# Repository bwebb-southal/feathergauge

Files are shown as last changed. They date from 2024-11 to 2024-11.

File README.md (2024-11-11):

# DIY Feather v4 Standard Operating Procedures 

Bret Webb (bwebb@southalabama.edu)

GitHub: https://github.com/bwebb-southal/feathergauge 

DesignSafe: coming soon

## Arduino IDE Preparation
If you have zero experience using the Arduino IDE, please refer to these tutorials [here](https://www.arduino.cc/en/Tutorial/HomePage)

1. Enable support for Adafruit boards in the Preferences menu by following [these directions](https://learn.adafruit.com/adafruit-feather-32u4-adalogger/setup)

1. Add support for the Adafruit AVR boards using Board Manager under Tools/Boards using [these instructions](https://learn.adafruit.com/adafruit-feather-32u4-adalogger/setup)

1. Select the Adafruit Feather 32u4 under Tools / Board

1. If this is your first time setting up your Arduino environment, you’ll need to add the necessary libraries. Libraries are managed using Tools / Manage Libraries in the Arduino IDE. The Nov2024 versions of the logger code sketches are compatible with the following libraries, and all of these need to be installed on your computer:

    a. Blue Robotics MS5837 v1.1.1

    b. SD v1.3.0

    c. RTClib v2.1.4

    d. TimerOne v1.1.1

1. Add the logger code sketch to your default Arduino Sketchbook location folder… note that the code sketch must reside in a folder of the same name as the sketch… this is required! The Arduino Sketchbook location folder was established during the setup process when you installed the Arduino IDE software. However, it can be redefined at any time. This is defined in your Arduino IDE Preferences menu (File / Preferences).

1. Ensure device is recognized in Tools/Port and select it. If you do not see your device, refer to Troubleshooting below. 

>[!NOTE]
> Ensure that your files and software are installed on your computer and not in a cloud-based segment of your PC or Mac. We have observed inconsistent behavior when using cloud-based folders. Note that many new PCs, specifically laptops, will default to cloud-based or cloud-connected folders on your system. If your Arduino Sketchbook location folder is not defined in a path structure on your physical hard drive, things may not work very well.

## Deployment Preparation 
Here are step-by-step instructions for preparing a DIY Feather v4 wave gauge for deployment. These steps assume that you already have your Arduino and environment prepared. If this is your first time using the gauge, please refer to the section at the end of this document regarding Arduino IDE Preparation. 

1. charge the battery (plug the battery into the USB charging adapter, or plug the battery into the board and then plug the board into a computer or USB outlet)

1. check the RTC
   
    a. Connect the board to the computer
  
    b. Open the Arduino software
  
    c. Open the sketch File/Examples/RTClib/ds3231
  
    d. Compile and upload the sketch to your board
  
    e. Open the serial monitor in the Arduino IDE (Tools / Serial Monitor) and confirm the date and time
  
    f. If the date/time is incorrect, uncomment line #25 then repeat steps 2d and 2e
  
    g. If the clock is still not correct, proceed to 3 below

1. reset the RTC

    a. remove coin cell battery for at least 60 seconds then replace it
  
    b. repeat steps 2c-2e

1. upload logger sketch

    a. There are four possible logger sketches as of Nov 2024: 1) rapid start with user-defined sampling rate; 2) delayed start with user-defined sampling rate; 3) rapid start with burst sampling; 4) delayed start with burst sampling
  
    b. Be sure to define your desired parameter values in the /* User Inputs */ section of each code sketch

1. allow DIY gauge to sample for about 60 s

1. disconnect usb 

1. remove microsd

1. insert microsd card into your computer

1. check data file and confirm that date/time and pressure (and/or temperature) are correct

1. remove data file(s)

1. reinsert microsd card into board

## Deployment 
When you are ready to deploy the gauge, follow these steps…

1. plug in the battery 

1. confirm LED flashing* (as of versions labeled _v1):

    a. rapid start, continuous sampling: solid green for about the first ~10 seconds then no other LEDs

    b. Rapid start, burst sampling: solid green during burst sampling; solid red during sleep interval 

    c. delayed start, continuous sampling: flashing red for ~20 seconds before start time; solid green for about the first ~10 seconds of continuous sampling

    d. delayed start, burst sampling: flashing red for ~20 seconds before start time; solid green during burst sampling; solid red while sleeping in between bursts

1. insert components into gauge housing along with a small desiccant pack

1. allow to sample** in atmospheric pressure for at least 1-2 minutes

1. place all prepared gauges in a bucket filled with your seawater (preferably from your deployment location but freshwater will do) and allow to sample** for at least 1-2 minutes. Ensure all sensors are oriented similarly (sensor at the bottom of the bucket).
   
1. deploy sensor making sure you keep depth attenuation in mind… see guidance below.

    a. Basically, you need to ensure your pressure sensor will detect the dynamic pressure fluctuations of your shortest wave periods, which attenuate quickly over the water column. 

    b. Figure 1 below shows the pressure decay coefficient as a function of wave period and water depth for four different deployment elevations (above the bed). You want to keep your decay coefficient as close to 1 as possible. You definitely want to stay out of the blue areas in these figures.

    c. Example: if you deploy a gauge on the bed in 3 m of water, you won’t detect any dynamic pressure (or hardly any) for wave periods less than or equal to 2 s. 

1. recommend deploying the gauge horizontally or vertically, and if vertically do so with sensor port pointing downward 

>[!NOTE]
> In step 2: if you would like to conserve more battery power, disabling the LED flashing is a fairly simple task. Any/all commands labeled “digitalWrite(----)” within the void loop() structure can be commented out with no impact to the code operation whatsoever. To comment (i.e., disable) out the LED blinking, simply place your cursor on the line of code (to the left of) containing the active digitalWrite(8, xxx) or digitalWrite(13, xxx) command, then select Edit / Comment/Uncomment from the Arduino IDE menu. If the line is active, it will become inactive, you’ll see  two “//” before the statement, and the text will turn gray. To reactivate that line of code, either remove the “//” or select Edit / Comment/Uncomment again and the line of code will become active once again.

>[!NOTE]
> In steps 4-5: this only makes sense if you are using the rapid start version of the logger code sketches. If you are using the rapid start code with burst sampling, make sure you are logging atmospheric and bucket test pressures during your burst interval (refer to LED flashing codes above for reference). If you are using the delayed start version of the code sketches, it may not be possible to sample atmospheric or bucket test pressures prior to deployment. If that is the case, I strongly recommend doing these things at the end of your deployment (before removing the battery). The atmospheric and bucket test pressure samples allow you to perform minor corrections to ensure consistent measurement values across your gauges. The inexpensive pressure sensors seem to have small offsets that, while not necessary, could be advantageous to correct by comparing their values under static conditions.

pressuredecayguide
Figure 1. Deployment Guidance for Pressure Attenuation with Depth

## Post-Deployment Recovery
Here are some suggested step-by-step procedures to consider after you retrieve your DIY wave gauge…

1. do not open gauge before cleaning thoroughly 

1. submerge gauge in a bucket of warm water mixed with distilled white vinegar (and dish soap if you like, but the dish soap is not necessary)

1. if gauges are considerably fouled, consider adding baking soda as this will combine with the vinegar to produce strong agitation and fizzing (definitely do not use dish soap here)

1. do not touch the gel membrane inside of the pressure sensor no matter what you do 

1. remove from cleaning bath and wipe dry

1. remove cap 

1. inspect for signs of moisture 

1. remove internal components 

1. disconnect battery 

1. remove microsd card

## Post-Processing 
The gauge data will be saved to CSV files on the microsd card. Post-processing the pressure data can be done in a variety of ways. We have posted some example post-processing scripts written in MATLAB. If you don’t have access to MATLAB you might find your own alternative method for processing the data. Just remember that the pressure values are absolute… so you need to subtract out atmospheric pressure. Ideally, you would have an atmospheric reference nearby so that you have a time-series of data, but in a pinch you can use an average/estimated value of atmospheric pressure. Each millibar of atmospheric pressure corresponds to (approximately) 1 cm of water height change. 

1. insert microsd card into your computer 

1. save the files to your computer

1. run the MATLAB post-processing scripts or process using your own codes

## Troubleshooting

1. My board isn’t recognized by Arduino IDE: make sure you are using a power+data cable… many micro USB cables are power only… if the device is not recognized as a com port under device manager (windows) then you’re probably using a power only cable.

1. My board isn’t recognized by Arduino IDE and I am sure that I am using an appropriate power+data cable: try resetting the bootloader on the feather logger board (see below).

1. I need to reset my bootloader: you’ll need access to the small black reset button located near the micro USB plug on top of the board. With the board plugged in, open the blink sketch found in File / Examples / Basics / Blink. Click the compile/upload “arrow” icon. Immediately double tap the reset button. This should resolve the issue. You may need to do this a few times. 

1. My date/time are incorrect: refer to 2 and 3 in the Deployment Preparation section above.

1. My logger isn’t working correctly: try uploading something simple like File / Examples / Basics / Blink. Does that work? If not, there’s likely an issue with your board. If yes, see below.

1. My logger still isn’t working: 

    a. Check your microsd card. Is it installed correctly? Are you using the recommended 8gb microsd card? If not, this may be the issue. The logger cannot handle large microsd cards.

    b. Check your wiring. 

    c. Perform a continuity check.

1. My logger is writing to the microsd card, but the values don’t make sense.

    a. Check your wiring… make sure you did not reverse the SCL and SDA wires.

    b. Try using the simple sketch provided by the MS5837 pressure sensor manufacturer by going to File / Examples / BlueRobotics MS5837 Library / MS5837_example. Before uploading, you’ll need to change one line in the code. Refer to the line with…

    ```
      sensor.setModel(MS5837::MS5837_30BA);
    ```
    and change the _30BA to _02BA as follows…
    ```
	    sensor.setModel(MS5837::MS5837_02BA);
    ```
    then open Serial Monitor and see if the values make sense.

1. open for addressing future issues…

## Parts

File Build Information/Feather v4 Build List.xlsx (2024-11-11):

USA Feather Logger v4 Parts List
ITEM | NAME | UNIT COST | UNITS | TOTAL ITEM COST | LINK
1 | Adafruit Feather 32u4 Adalogger | $21.95 | 1 | $21.95 | https://www.adafruit.com/product/2795
2 | Adafruit DS3231 Precision RTC - STEMMA QT | $13.95 | 1 | $13.95 | https://www.adafruit.com/product/5188
3 | STEMMA QT / Qwiic JST SH 4-Pin Cable - 50mm Long | $0.95 | 1 | $0.95 | https://www.adafruit.com/product/4399
4 | STEMMA QT / Qwiic JST SH 4-Pin Cable - 200mm Long | $1.25 | 1 | $1.25 | https://www.adafruit.com/product/4401
5 | Lithium Ion Battery Pack 3.7V 4400 mAh | $19.95 | 1 | $19.95 | https://www.adafruit.com/product/354
6 | Micro Lipo-USB Lilon/LiPoly charger v2 | $5.95 | 1 | $5.95 | https://www.adafruit.com/product/1304
7 | CR1220 12mm Diameter Coin Cell Battery | $0.95 | 1 | $0.95 | https://www.adafruit.com/product/380
8 | SD/MicroSD Memory Card 86B SDHC | $9.95 | 1 | $9.95 | https://www.adafruit.com/product/1294
9 | Bar02 Ultra High Resolution 10m Depth/Pressure Sensor | $75.00 | 1 | $75.00 | https://bluerobotics.com/store/sensors-cameras/sensors/bar02-sensor-r1-rp/
10 | 1.5" PVC Pipe | $2.17 | 0.67 | $1.45 | https://www.lowes.com/pd/Charlotte-Pipe-1-1-2-in-dia-x-5-ft-L-330-PSI-PVC-Pipe/3133039
11 | 1-1/2-in dia PVC Female Adapter Fitting | $2.29 | 1 | $2.29 | https://www.lowes.com/pd/Charlotte-Pipe-1-1-2-in-x-1-1-2-in-dia-PVC-Schedule-40-Female-Adapter-Fitting/3132709
12 | 1-1/2-in PVC DWV Male Plug | $1.69 | 1 | $1.69 | https://www.lowes.com/pd/Charlotte-Pipe-1-1-2-in-x-1-1-2-in-dia-PVC-Schedule-40-Male-Cleanout-Plug-Fitting/3354904
13 | Oatey 1-1/2-in Gripper PVC DWV Test Plug | $5.65 | 1 | $5.65 | https://www.lowes.com/pd/Oatey-Gripper-1-1-2-in-x-1-1-2-in-x-1-1-2-in-x-1-1-2-in-dia-PVC-Schedule-40-Test-Plug-Fitting/3824165
14 | PVC Glue & Primer | $11.68 | 0.01 | $0.12 | https://www.lowes.com/pd/Oatey-Handypack-8-fl-oz-PVC-Cement-and-Primer/4750411
15 | LOCTITE Waterproof Sealant 2.7-fl oz Gel | $6.48 | 0.05 | $0.32 | https://www.lowes.com/pd/Henkel-Waterproof-Sealant-2-7-fl-oz-Gel-Silicone-Multipurpose-Adhesive/5004266381
16 | VELCRO Brand 0.875-in Sticky Back Squares Hook and Loop Fastener (12-Pack) | $0.36 | 1 | $0.36 | https://www.lowes.com/pd/VELCRO-12-Pack-0-875-in-Black-Fastener/3020016
17 | Screws for MCU and RTC M2 x 25 50 pk | $0.19 | 4 | $0.74 | https://www.mcmaster.com/catalog/130/3484/92010A111
18 | Nuts for MCU and RTC M2 100 pk | $0.06 | 4 | $0.25 | https://www.mcmaster.com/catalog/130/3634/91828A111
19 | Internal MCU+Battery Mount Part 1 | $0.00 | 1 | $0.00 | See GitHub Page
20 | Internal MCU+Battery Mount Part 2 | $0.00 | 1 | $0.00 | See GitHub Page
 |  |  |  | $162.77
optional | Desiccant pack | $0.17 | 1 | $0.17 | https://www.amazon.com/dp/B01M7V19JE?ref=fed_asin_title&th=1

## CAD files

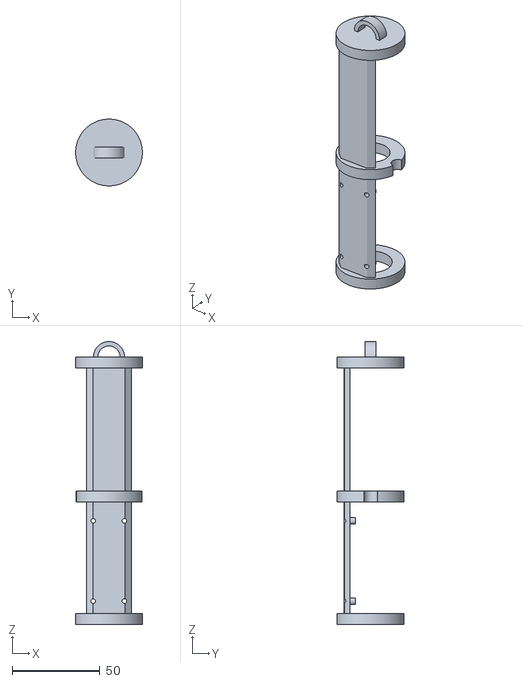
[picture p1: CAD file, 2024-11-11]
Build Information/Internal Component Part 1/USA_Wave_Gage_Insert_003v3.stl
38.1 x 38.1 x 161.3

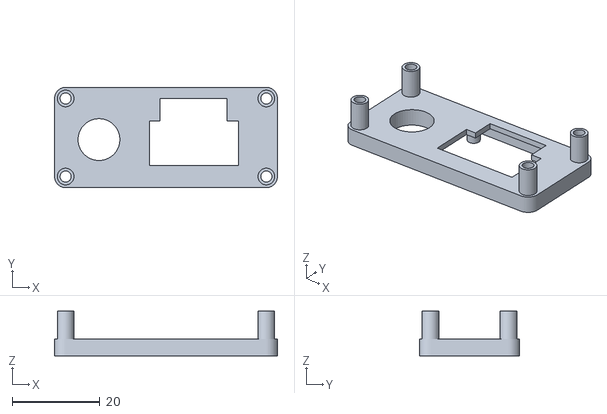
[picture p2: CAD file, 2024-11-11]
Build Information/Internal Component Part 2/rtc_feather_stacker v8.stl
50.8 x 22.9 x 10.2

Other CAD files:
Build Information/Internal Component Part 1/USA_Wave_Gage_Insert_003v3.f3d

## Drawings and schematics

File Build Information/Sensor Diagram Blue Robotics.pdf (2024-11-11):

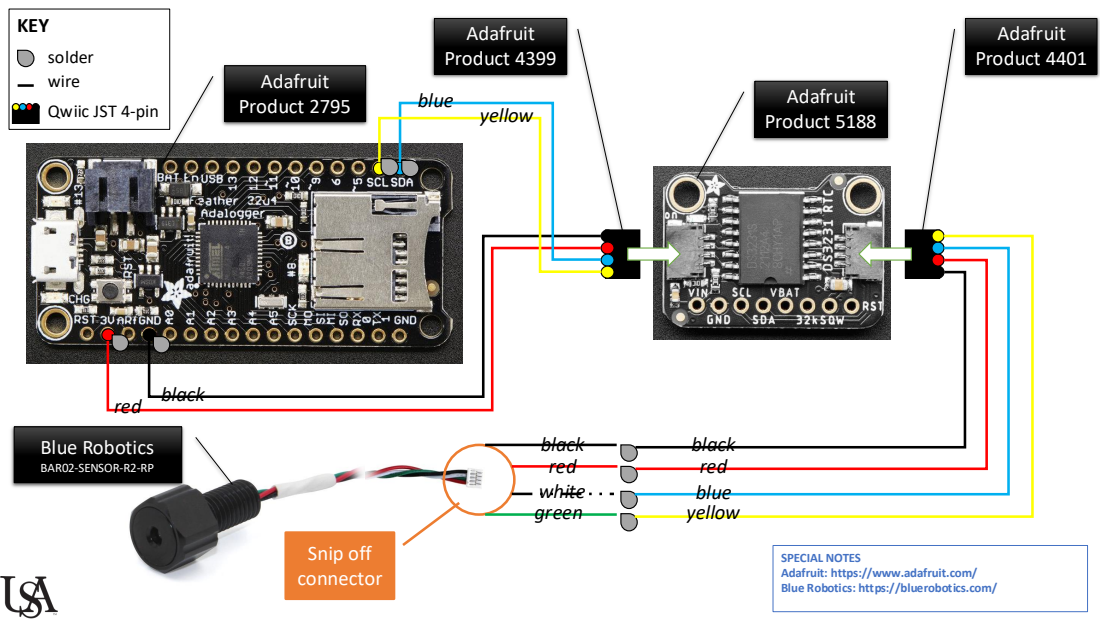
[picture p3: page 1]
Snip off connector; black red; green; white; blue; yellow; black; red; Adafruit Product 4399; Adafruit Product 5188; Adafruit Product 4401; Adafruit Product 2795; Blue Robotics; BAR02-SENSOR-R2-RP

KEY
solder
wire
Qwiic JST 4-pin

SPECIAL NOTES
Adafruit: https://www.adafruit.com/
Blue Robotics: https://bluerobotics.com/

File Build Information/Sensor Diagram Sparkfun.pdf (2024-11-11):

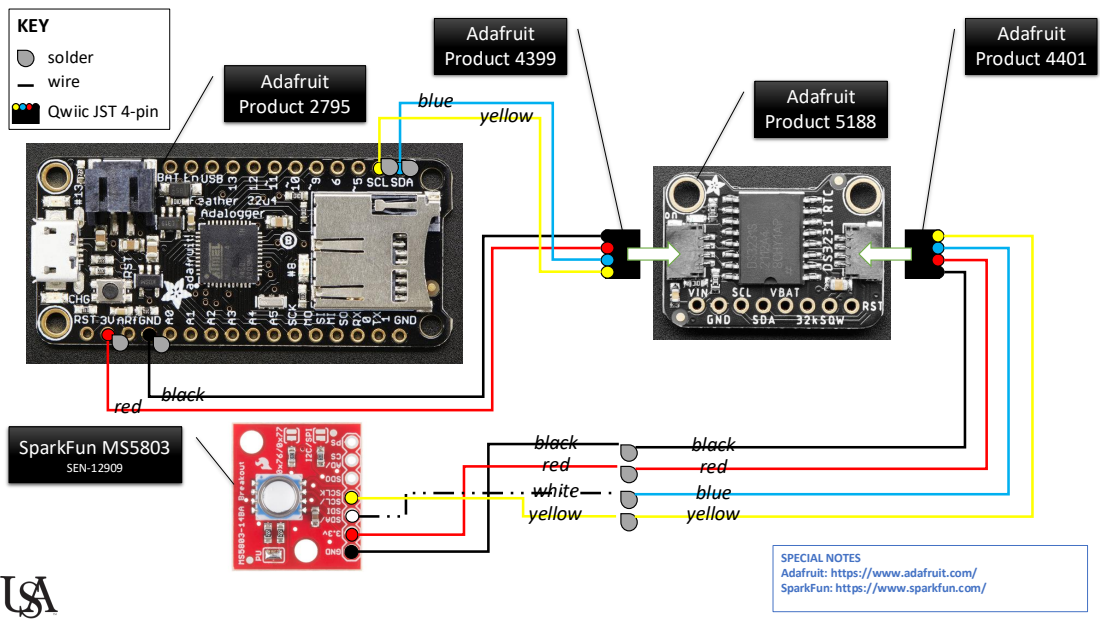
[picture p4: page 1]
white; black red; blue; yellow; Adafruit Product 4399; Adafruit Product 5188; Adafruit Product 4401; Adafruit Product 2795; SparkFun MS5803; SEN-12909; red; black

KEY
solder
wire
Qwiic JST 4-pin

SPECIAL NOTES
Adafruit: https://www.adafruit.com/
SparkFun: https://www.sparkfun.com/

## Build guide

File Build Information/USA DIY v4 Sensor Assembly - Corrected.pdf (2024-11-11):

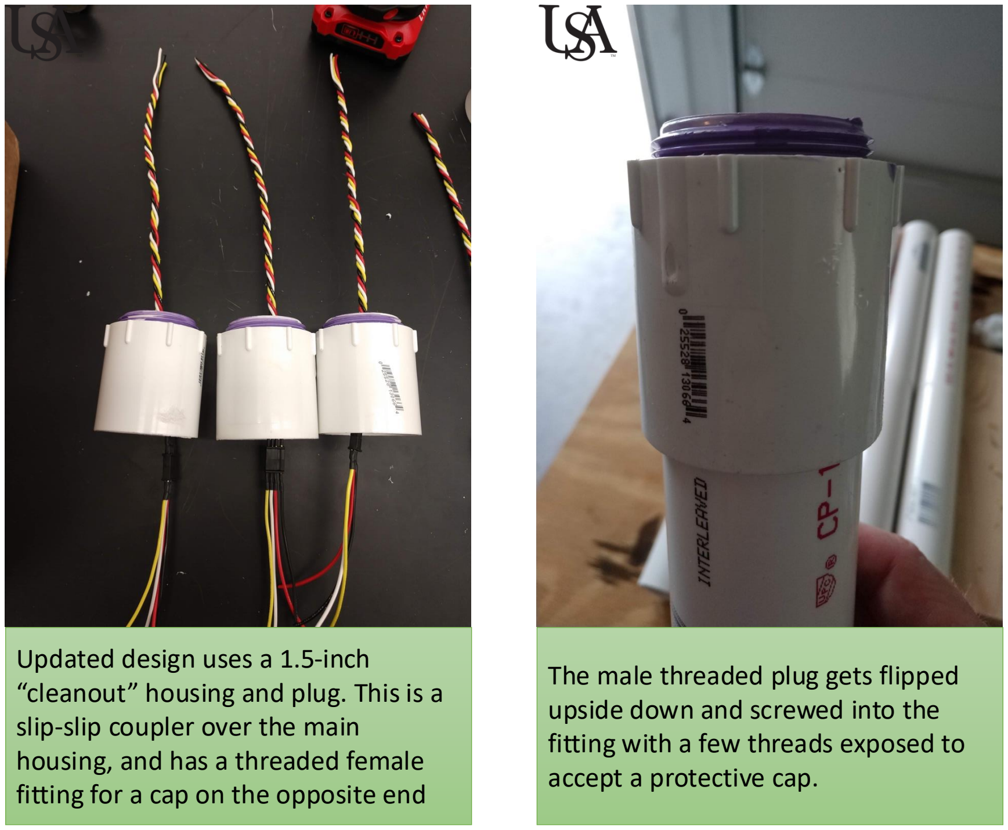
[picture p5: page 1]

Updated design uses a 1.5-inch “cleanout” housing and plug. This is a slip-slip coupler over the main housing, and has a threaded female fitting for a cap on the opposite end

The male threaded plug gets flipped upside down and screwed into the fitting with a few threads exposed to accept a protective cap.

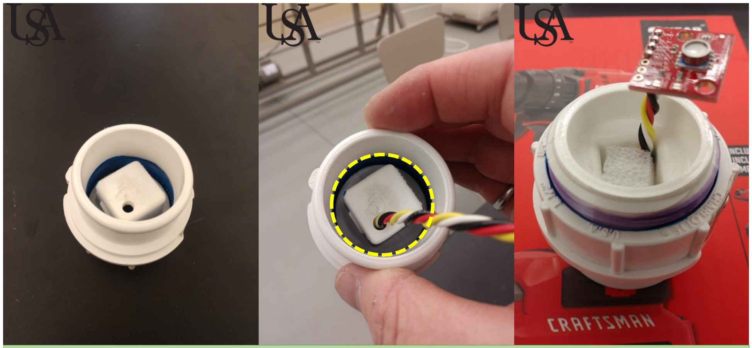
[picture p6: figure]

A small hole is drilled through the plug cap to thread the sensor breakout wires. The sensor is then soldered to the wire leads. The sensor board is bedded in small amount of epoxy putty and then the entire area is flooded with flowable epoxy. I place a small piece of foam in the cleanout plug recess to take up space and prevent the epoxy putty from settling. I also like to add flowable epoxy on the back side (see yellow dashed circle middle photo) above the PVC threads for added safety. This step is probably not necessary.

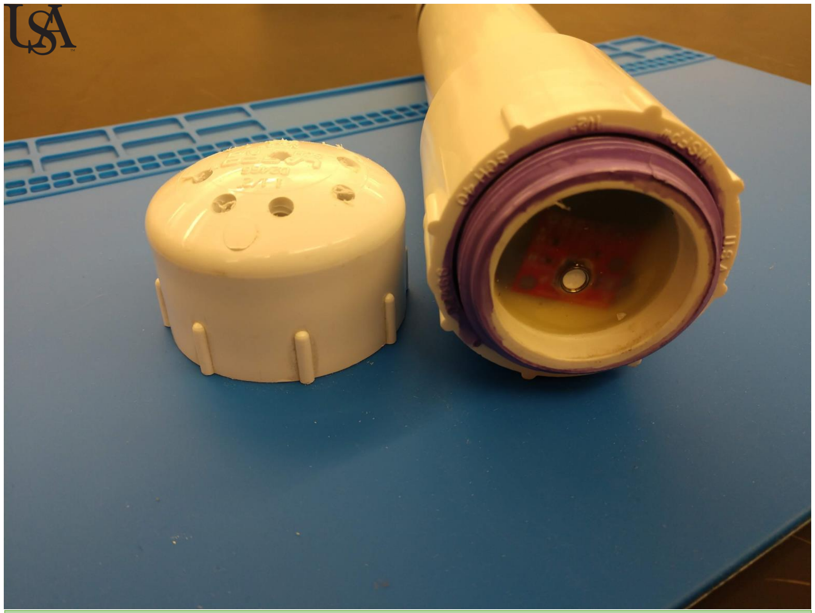
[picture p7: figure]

Photo of final assembly with sensor board potted in epoxy. The threaded cap (left) can be screwed down over the exposed cleanout plug threads to protect the exposed MEMS sensor membrane/gel.

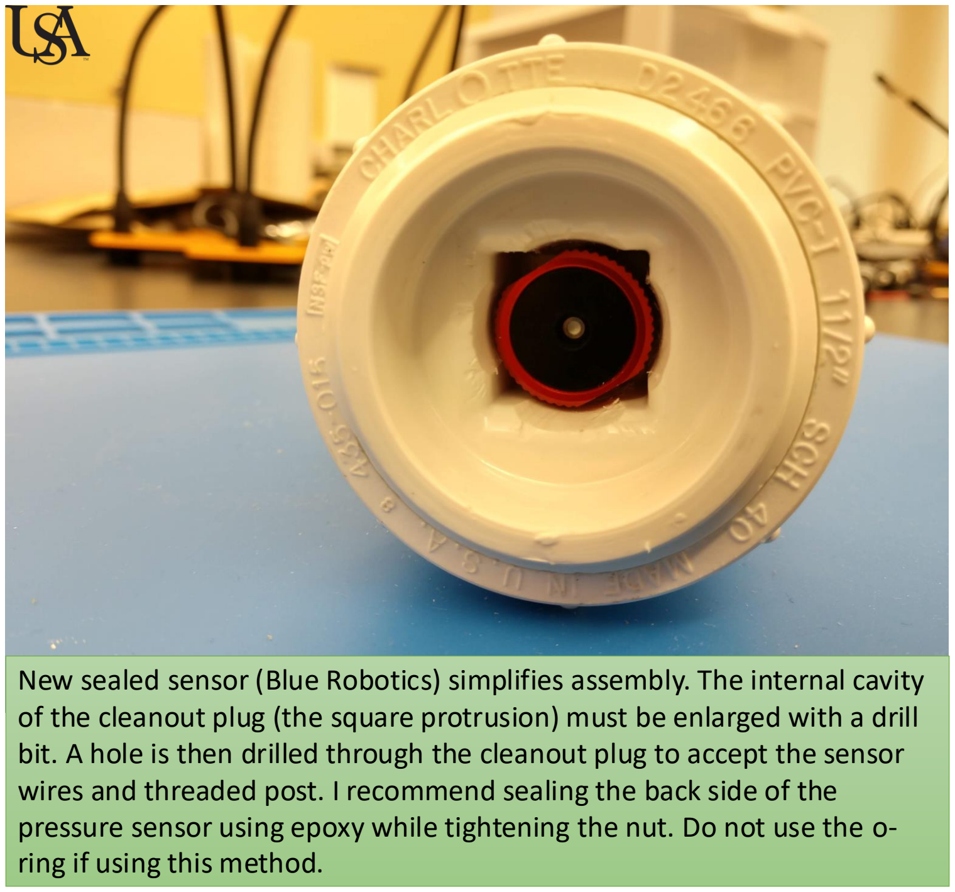
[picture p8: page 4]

New sealed sensor (Blue Robotics) simplifies assembly. The internal cavity of the cleanout plug (the square protrusion) must be enlarged with a drill bit. A hole is then drilled through the cleanout plug to accept the sensor wires and threaded post. I recommend sealing the back side of the pressure sensor using epoxy while tightening the nut. Do not use the o-ring if using this method.

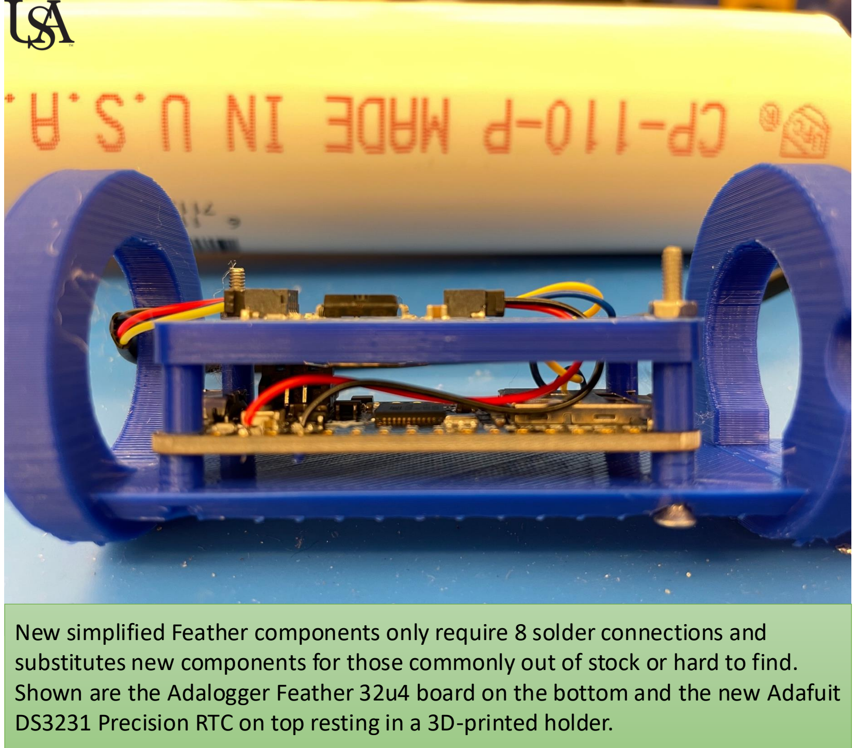
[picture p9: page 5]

New simplified Feather components only require 8 solder connections and substitutes new components for those commonly out of stock or hard to find. Shown are the Adalogger Feather 32u4 board on the bottom and the new Adafuit DS3231 Precision RTC on top resting in a 3D-printed holder.

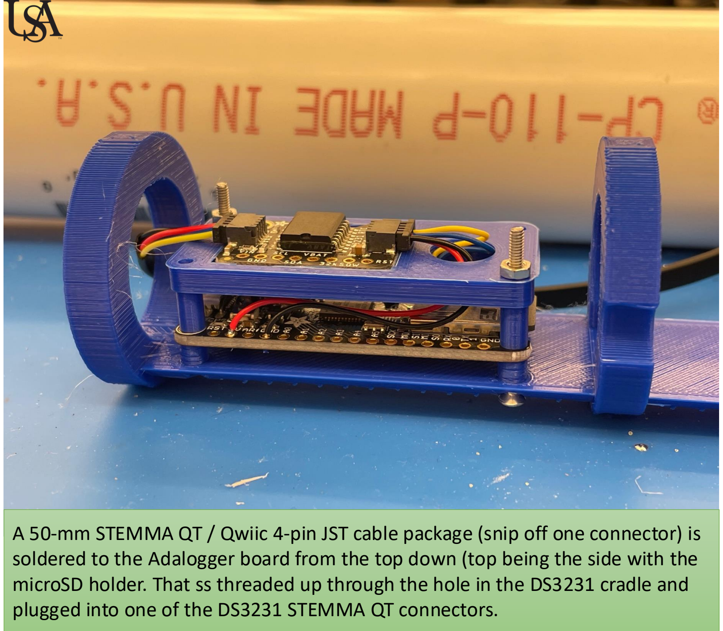
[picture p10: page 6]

A 50-mm STEMMA QT / Qwiic 4-pin JST cable package (snip off one connector) is soldered to the Adalogger board from the top down (top being the side with the microSD holder. That ss threaded up through the hole in the DS3231 cradle and plugged into one of the DS3231 STEMMA QT connectors.

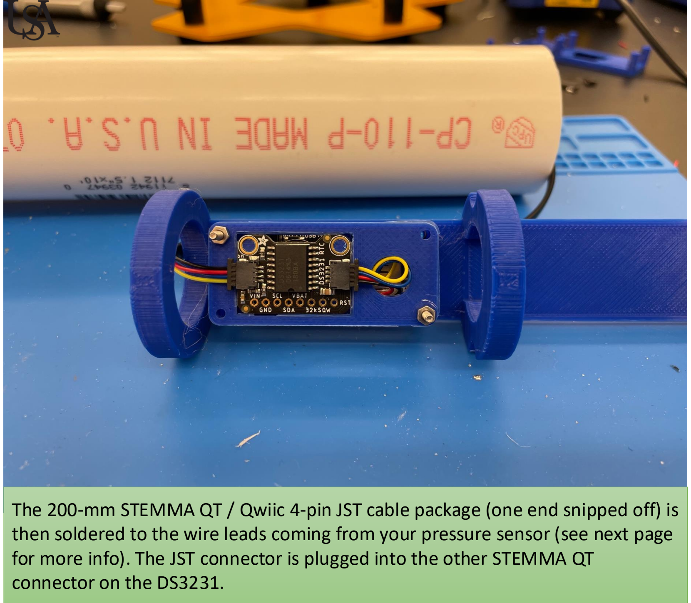
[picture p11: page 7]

The 200-mm STEMMA QT / Qwiic 4-pin JST cable package (one end snipped off) is then soldered to the wire leads coming from your pressure sensor (see next page for more info). The JST connector is plugged into the other STEMMA QT connector on the DS3231.

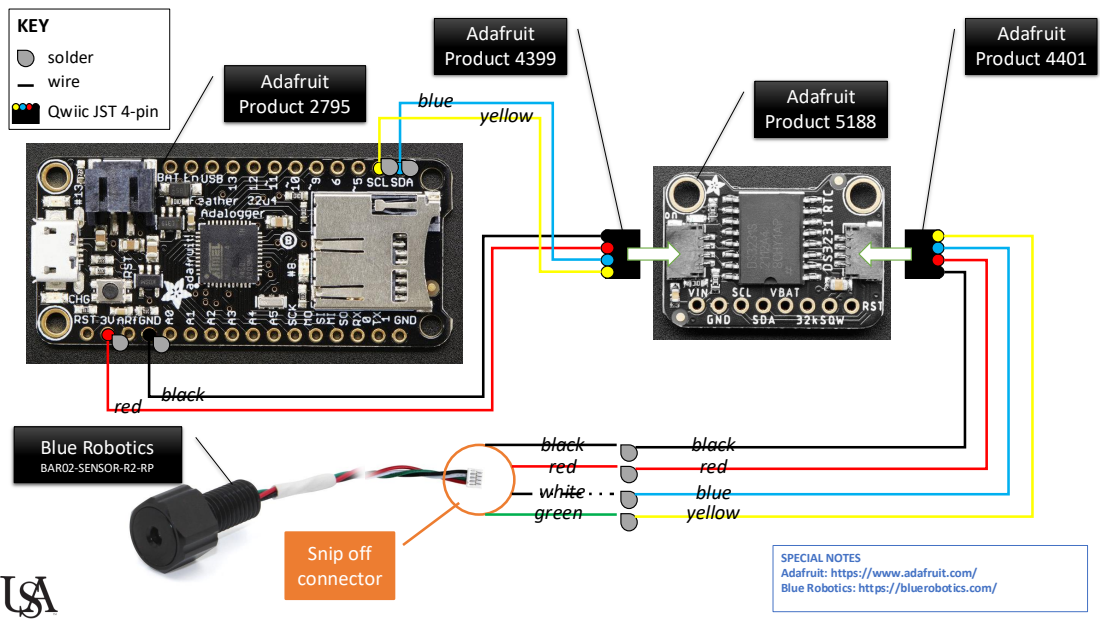
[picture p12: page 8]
Snip off connector; black red; green; white; blue; yellow; black; red; Adafruit Product 4399; Adafruit Product 5188; Adafruit Product 4401; Adafruit Product 2795; Blue Robotics; BAR02-SENSOR-R2-RP

KEY
solder
wire
Qwiic JST 4-pin

SPECIAL NOTES
Adafruit: https://www.adafruit.com/
Blue Robotics: https://bluerobotics.com/

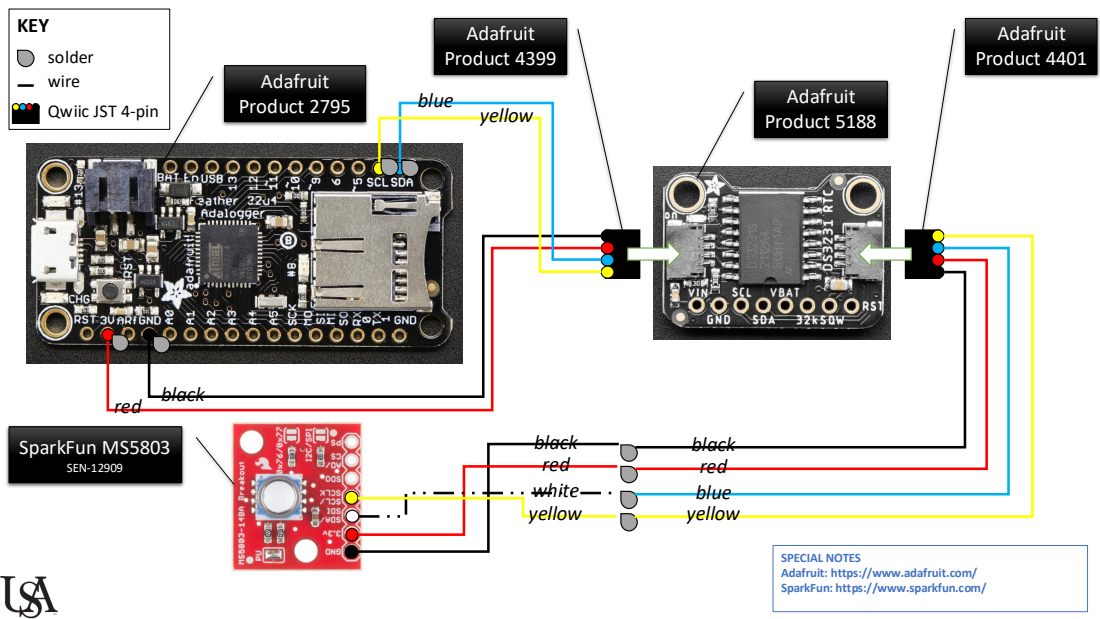
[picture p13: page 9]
white; black red; blue; yellow; Adafruit Product 4399; Adafruit Product 5188; Adafruit Product 4401; Adafruit Product 2795; SparkFun MS5803; SEN-12909; red; black

KEY
solder
wire
Qwiic JST 4-pin

SPECIAL NOTES
Adafruit: https://www.adafruit.com/
SparkFun: https://www.sparkfun.com/

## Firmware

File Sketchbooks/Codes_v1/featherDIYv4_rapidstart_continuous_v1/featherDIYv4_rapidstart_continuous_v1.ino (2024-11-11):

#include <Wire.h>
#include <SD.h>
#include "MS5837.h"
#include <RTClib.h>
#include <TimerOne.h>

/* User Inputs */
float sampleFreq = 10; // sampling frequency in Hz

#define cardSelect 4 // for SD card
MS5837 pressuresensor; //Initializing global variables
RTC_DS3231 rtc;
File datafile;

// Pin where the battery voltage is read
const int batteryPin = A9;  // Replace with the correct analog pin

// Reference voltage for the ADC (3.3V or 5V depending on your setup)
const float referenceVoltage = 3.3;

// The max ADC value for a 10-bit ADC (0-1023)
const int maxADCValue = 1024;

//Set Variables for Intermittant SD logging
String Stringfile = String("");
int n=1;
int j=1;
int k=1;
volatile boolean flag = true;
int Year,Month,Day,Hour,Minute,Second; // variables to differentiate time elements
char filename[15]; //Creates an array of size 15 filled with elements of type 'char'

void dateTime(uint16_t* date, uint16_t* time) { //Void function for timestamp of .csv file
    DateTime now = rtc.now();
    *date = FAT_DATE(now.year(), now.month(), now.day());
    *time = FAT_TIME(now.hour(), now.minute(), now.second());
  }

void error (uint8_t errno) { //This will trigger the LED on pin 13 to blink a certain number of times. This is used to troubleshoot the code.
  while (1) {
  uint8_t i;
  for (i = 0; i < errno; i++) {
    digitalWrite(13, HIGH);
    delay(100);
    digitalWrite(13, LOW);
    delay(100);
    }
  for (i = errno; i < 10; i++) {
    delay(200);
    }
  }
}

void setup() {
  pinMode(13, OUTPUT); //This activates the red LED on pin 13
  pinMode(8, OUTPUT); //This activates the green LED on pin 8
  Serial.begin(9600);
  Serial.println("Starting!");
  Wire.begin();
  rtc.begin();
  pressuresensor.init();
  pressuresensor.setModel(MS5837::MS5837_02BA);
  pressuresensor.setFluidDensity(997); //Freshwater density = 997 kg/m^3 , Seawater density = 1029 kg/m^3
  Serial.print("Initializing SD card...");
  
  if (!SD.begin(cardSelect)) { //If sd card is not present then this if statement will be triggered
    Serial.println("Card Failed, or Not Present");
    error(1);
    return;
  }
  
  float sampleTime = (1/sampleFreq)*1000000; // convert sampling frequency to microseconds
  Timer1.initialize(sampleTime); // sampling interval in microseconds
  Timer1.attachInterrupt(timerIsr); // service routine

  Serial.println("Card Initialized.");
  strcpy(filename, "LOG00.CSV");
  for (uint8_t i = 0; i < 100; i++) { //This for loop is used to create a new .csv file everytime the sd card is pulled out of card holder
    filename[3] = '0' + i / 10;
    filename[4] = '0' + i % 10;
    if (! SD.exists(filename)) {
    break;
    }
  }
  SdFile::dateTimeCallback(dateTime); //This uses the void function that timestamps the .csv file
  datafile = SD.open(filename, FILE_WRITE); //Opens .csv file
  if (datafile) {
    datafile.print("Timestamp,\"Pressure [mbar]\",\"Temp [deg C]\",\"Battery [VDC]\"");
    datafile.println();
    Serial.println("Header logged");
    } else {
    Serial.println("error opening datalog-case1");
    error(5);
  }
  Serial.println("READY!");
  delay(500);
  Serial.println("Datalogging!");
}

void loop() {
    // Read the raw ADC value
    int sensorValue = analogRead(batteryPin);
  
  // Calculate the battery voltage
  // The actual voltage divider ratio should be adjusted as needed
  float batteryVoltage = (sensorValue * referenceVoltage) / maxADCValue;

  // If using a voltage divider, multiply by the ratio to get the actual voltage
  // e.g., if using a 2:1 divider, multiply by 2
  float actualBatteryVoltage = batteryVoltage * 2;  // Adjust multiplier based on your divider

  // Print the measured battery voltage to the Serial Monitor
  //Serial.print("Battery Voltage: ");
  //Serial.print(actualBatteryVoltage);
  //Serial.println(" V");
  
  if(n==11){
    Serial.print(Stringfile);
    datafile.print(Stringfile);
    datafile.flush();
    Stringfile.replace(Stringfile, "");
    n= n - 10;
  }
  else{ 
    // xxx
  }

  DateTime now = rtc.now();
  Year=now.year(); Month=now.month(); Day=now.day();
  Hour=now.hour(); Minute=now.minute(); Second=now.second();

    if(flag == true){
      Year=now.year(); Month=now.month(); Day=now.day();
      Hour=now.hour(); Minute=now.minute(); Second=now.second();
      pressuresensor.read();
      float temp2 = pressuresensor.temperature();
      float pres = pressuresensor.pressure();
      j=j+1;
      if (j <= 400) {
        digitalWrite(8, HIGH); //Turns on green LED light to ensure that code has processed through to this point.
      } else {
        digitalWrite(8, LOW); //Turns off the green LED light to conserve battery
      }

      Stringfile += (Year);
      Stringfile += ('/');
      Stringfile += (Month);
      Stringfile += ('/');
      Stringfile += (Day);
      Stringfile += (" ");
      Stringfile += (Hour);
      Stringfile += (':');
      Stringfile += (Minute);
      Stringfile += (':');
      Stringfile += (Second);
      Stringfile += (",");
      Stringfile += (pres);
      Stringfile += (",");
      Stringfile += (temp2);
      Stringfile += (",");
      Stringfile += (actualBatteryVoltage);
      Stringfile += ("\r\n");
      Serial.println("I am logging");
      flag = false;
      n = n + 1;
      j = j + 1;
    } else { 
      // do nothing
    }
}

void timerIsr() {
  flag = true;
  // just pause for logging interval... could put write statement here?
}
